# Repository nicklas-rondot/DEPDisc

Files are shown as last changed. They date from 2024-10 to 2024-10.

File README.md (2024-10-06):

# DEPDisc
The DEPDisc platform is the first implementation of dielectrophoresis where both the equipment and the consumables are truly inexpensive. It utilizes CD microfluidics to allow the integration of DEP with other microfluidic operations. 
All aspects of the DEPDisc platform are open-source, including the fabrication technique for the discs (with example designs) and the device.
While the paper presents the underlying theory and the results of the DEPDisc platform, this repository is intended to provide the necessary information to reproduce the platform.

This version is from the 06th of October 2024. A more current version might be available at https://github.com/nicklas-rn/DEPDisc.

## Table of Contents
- [Discs](#Discs)
- [Device](#Device)
- [How to Run](<#How to Run>)
- [Additional Figures](<#Additional Figures>)

## Discs
In the folder [Discs](/Discs), the design files for the discs can be found. The PCB files can be used in Eagle or Fusion360 Electronics. [Example Disc PCBs](/Discs/Example%20Disc%20PCBs) are provided as inspiration. The separate [coil PCB](/Discs/Coil%20PCB/) used as transmitter is included as well. For new designs, the [coil PCB library](/Discs/Coil%20PCB%20Library/) can be used.

## Device
The [Device CAD and PCB folder](/Device/) contains all the necessary files to reproduce the DEPDisc device. The device is composed of a PCB, off-the-shelf components, and a set of 3D printed parts. 

### PCB
To order the PCB at [JLCPCB](https://jlcpcb.com), the [Manufacturing folder](/Device/PCB/Manufacturing/) with a [ZIP file](/Device/PCB/Manufacturing/DEPDisc%20Base%20rev1%20v8_2024-09-17.zip) of the Gerber files is included. For assembly by JLCPCB, the [BOM file](/Device/PCB/Manufacturing/DEPDisc%20Base%20rev1%20v8_2024-09-17.zip) and [Pick and Place file](/Device/PCB/Manufacturing/DEPDisc%20Base%20rev1%20v8_2024-09-17.zip) are also provided. 
The ordering process is the follwing:
1. Go to [JLCPCB](https://jlcpcb.com)
2. Click on **Add gerber file** and upload the ZIP file
3. Select the desired options and **Enable PCB Assembly** (choose 2 as PCBA quantity instead of 5). Select **Bottom Side Assembly**.
4. After clicking **Next**, upload the **BOM file** and **CPL (Pick and Place) file**, then continue
5. When reviewing the parts, ensure that only C13 and JP3 show 'No part selected' and that the rest of the parts are correctly assigned. Then click **Next** and then **Do not Place** upon the prompt showing that the project has unselected parts.
6. Review the part placement and click **Next**, then click **Save to Cart**
7. Review the order and click **Secure Checkout**

The [design files](/Device/PCB/Design%20Files) of the PCB for Eagle or Fusion360 Electronics are included in case this project is used as inspiration or if modifications are desired.

### Housing
The [parts for printing](/Device/3D%20Printed%20Parts) are provided as STL files. In the slicer, we recommend enabling tree-supports. 
A [STEP file](/Device/DEPDisc%20Device%20rev1.step) of the assembly is included. 

### Assembly
To assemble the device, use the following procedure:
1. Place M3 nuts in all the provided slots in the 3D printed parts.
2. Solder the pin-headers to the PCB: 
3. Solder two jumper wires to the motor: 
4. Plug the ESP32 NodeMCU Dev board into the pin-headers: 
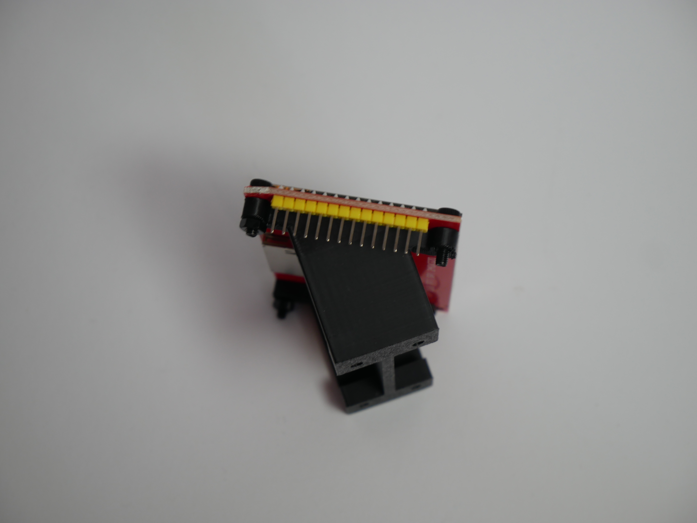
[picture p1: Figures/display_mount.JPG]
5. Screw the touch display to the display mount: 
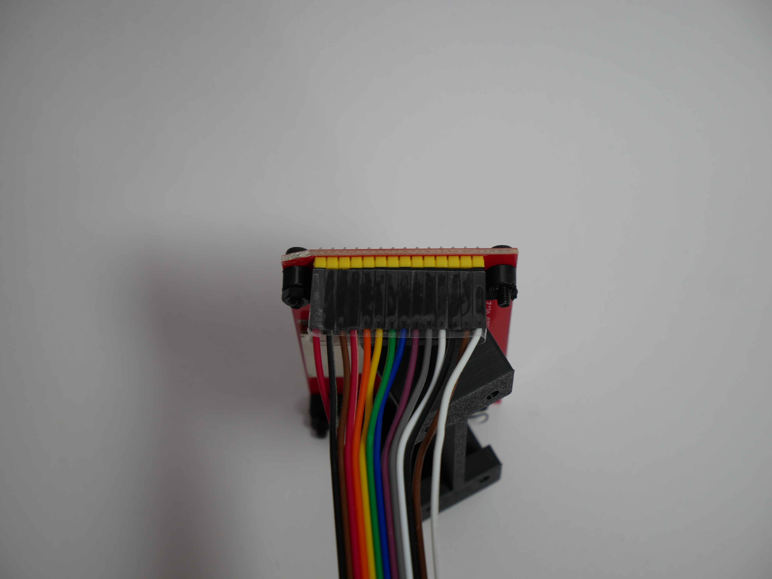
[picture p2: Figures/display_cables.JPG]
6. Plug in 14 female-to-female jumper wires to the display. We recommend placing tape around the ends to keep the wires together when they are removed: 
7. Plug the other side of the jumper wires into the PCB: 
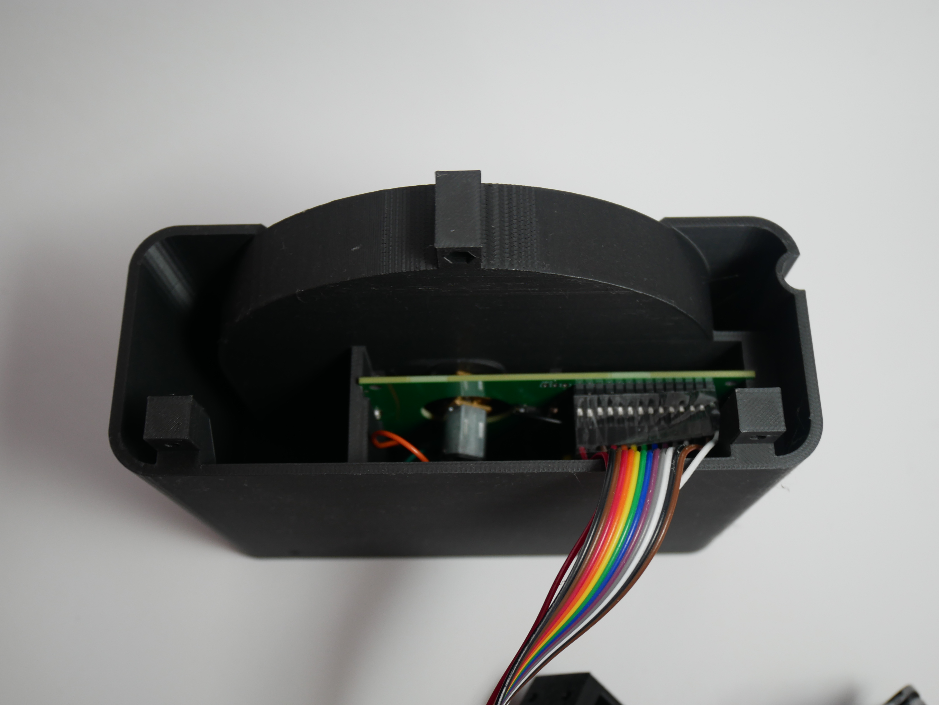
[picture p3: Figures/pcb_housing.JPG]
8. Slide the PCB into the left side of the inner shell of the housing and move the motor through the hole: 
9. Screw the motor in place with two M1.2 screws: 
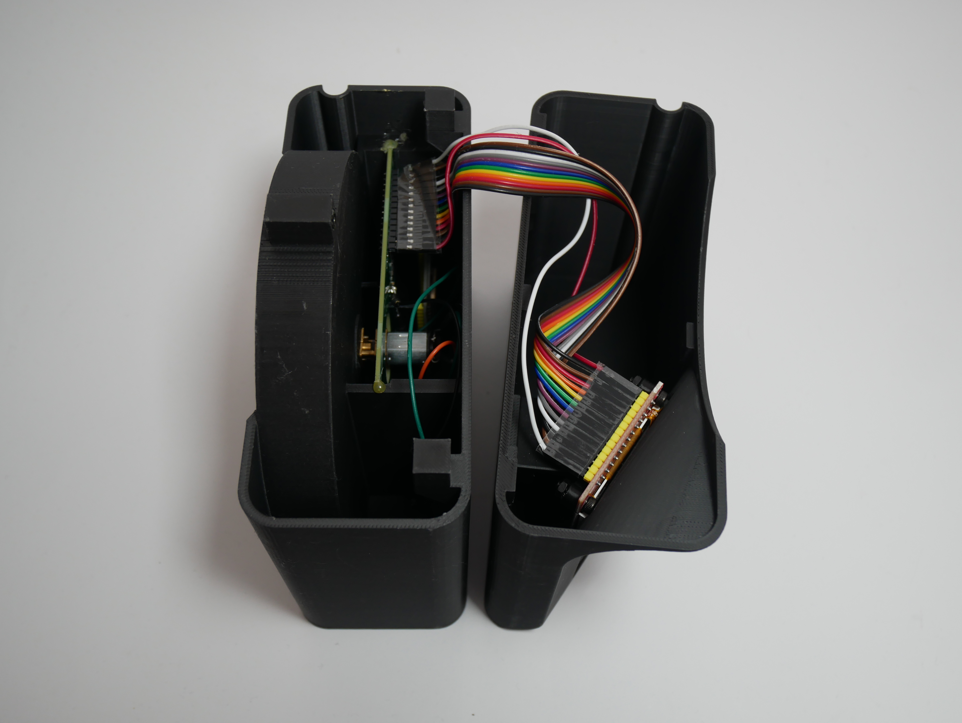
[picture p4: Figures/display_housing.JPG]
10. Slide the display in to the right side of the inner shell of the housing: 
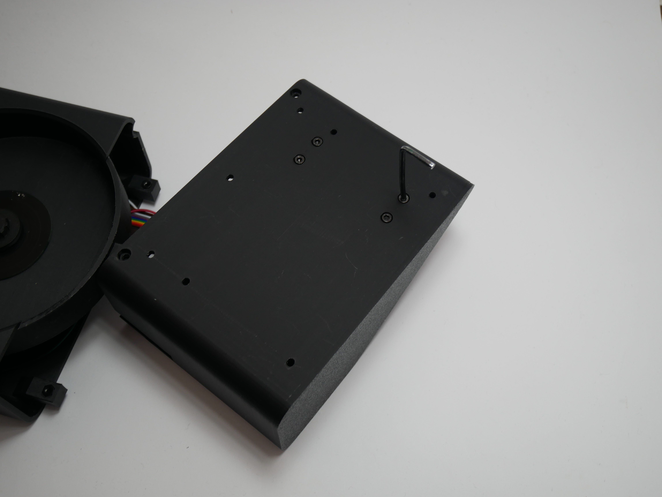
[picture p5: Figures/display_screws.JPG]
11. Screw the display in place from the bottom with four M3 screws: 
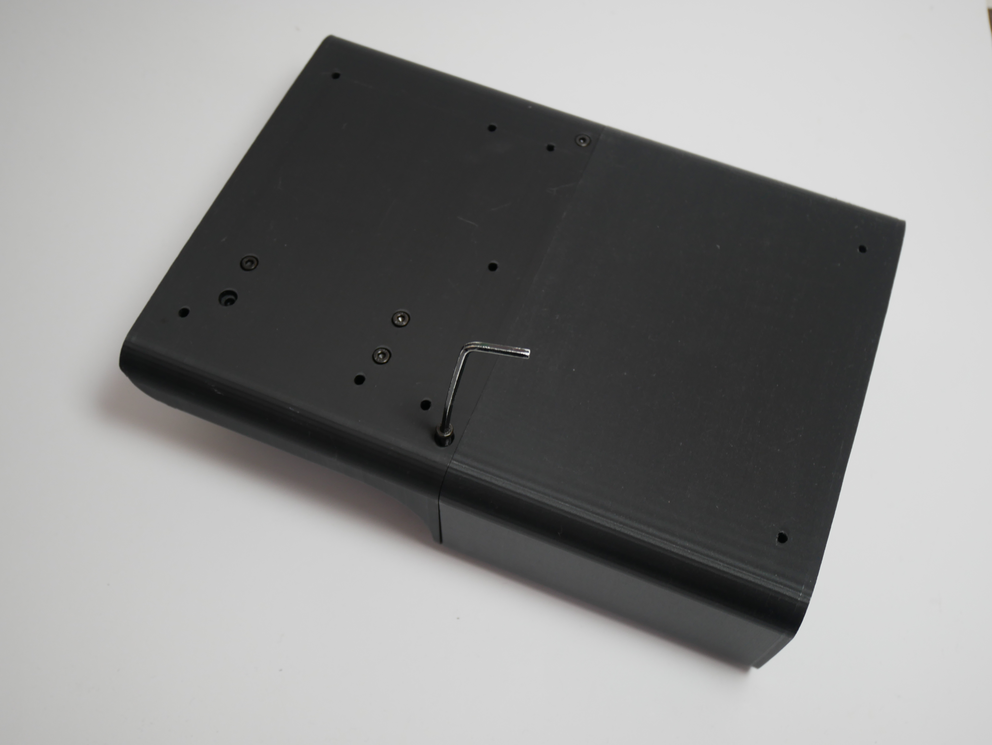
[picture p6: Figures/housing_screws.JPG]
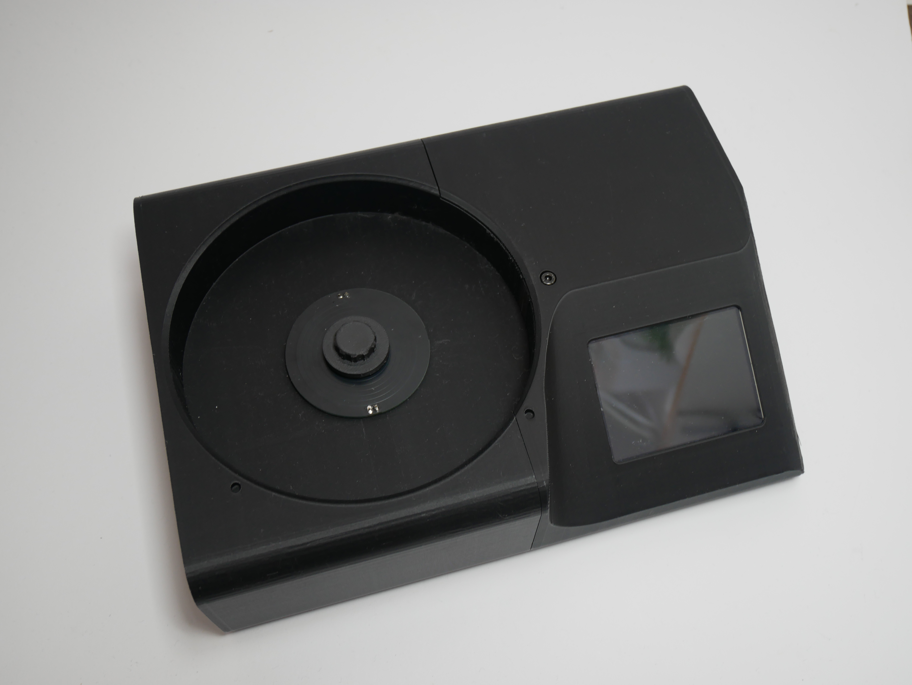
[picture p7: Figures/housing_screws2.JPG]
12. Connect the two inner shell sides with three M3 screws:  
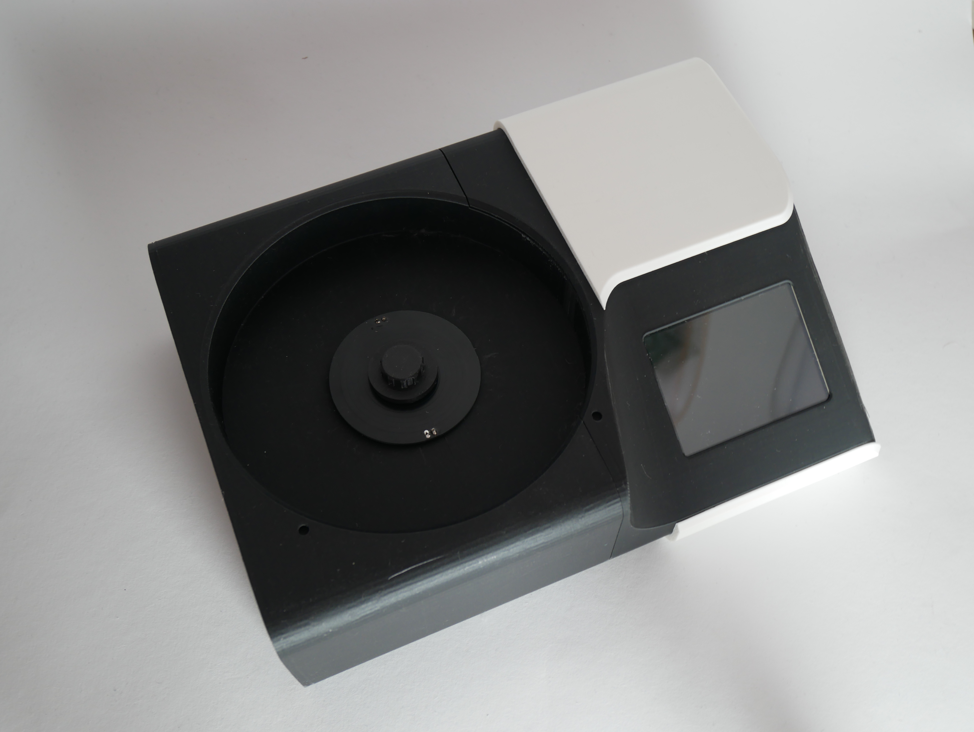
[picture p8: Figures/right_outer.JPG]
13. Place the right side of the outer shell on top of the inner shell by carefully bending it slightly: 
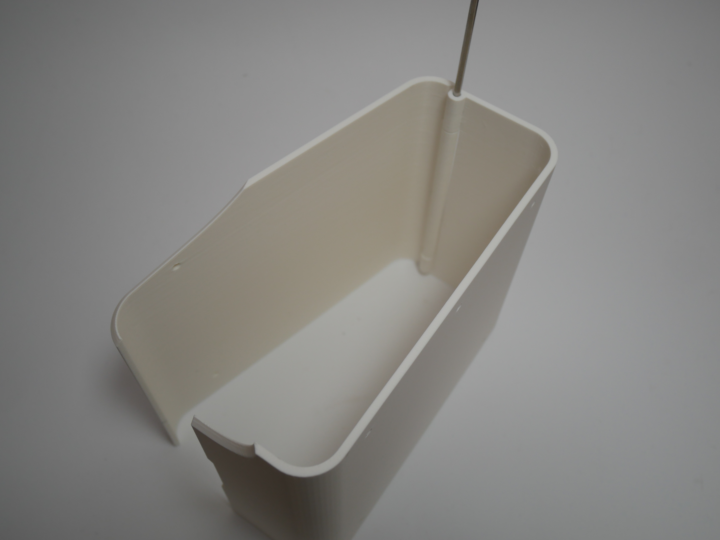
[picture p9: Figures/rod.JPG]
14. Push the aluminium rod through the left side of the outer shell and the hatch: 
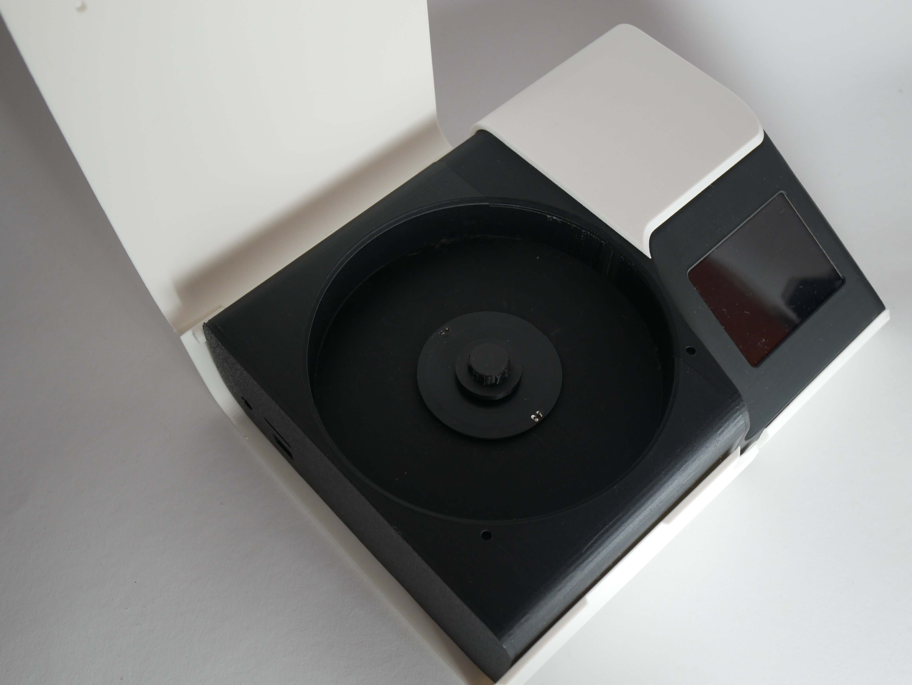
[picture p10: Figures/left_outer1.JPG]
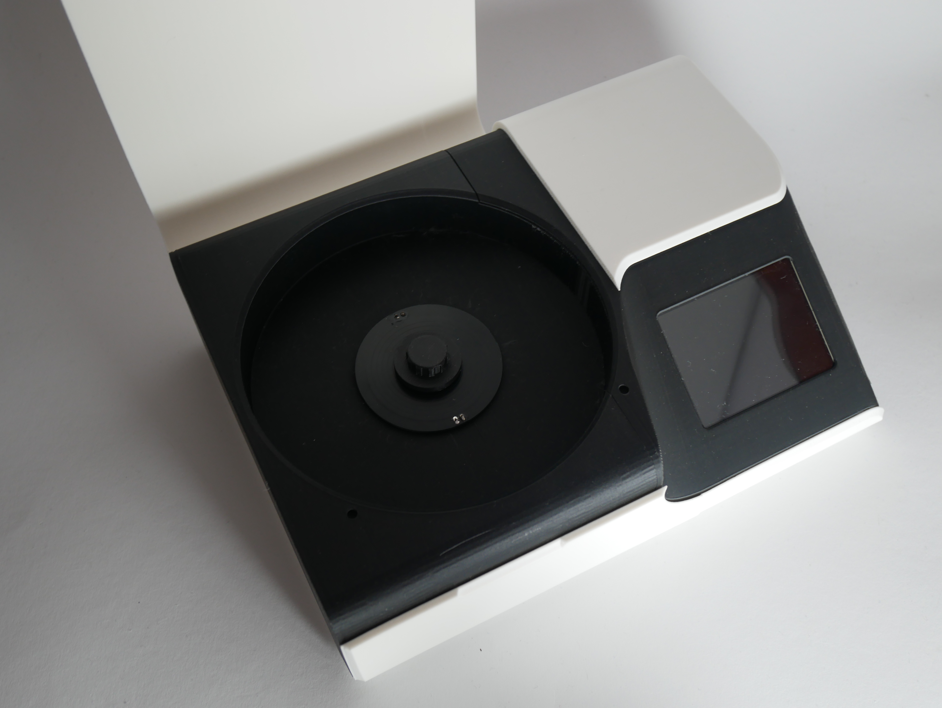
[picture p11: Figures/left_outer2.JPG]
15. Push the left side of the outer shell on top of the inner shell by moving it in from the left and carefully bending it slightly:  
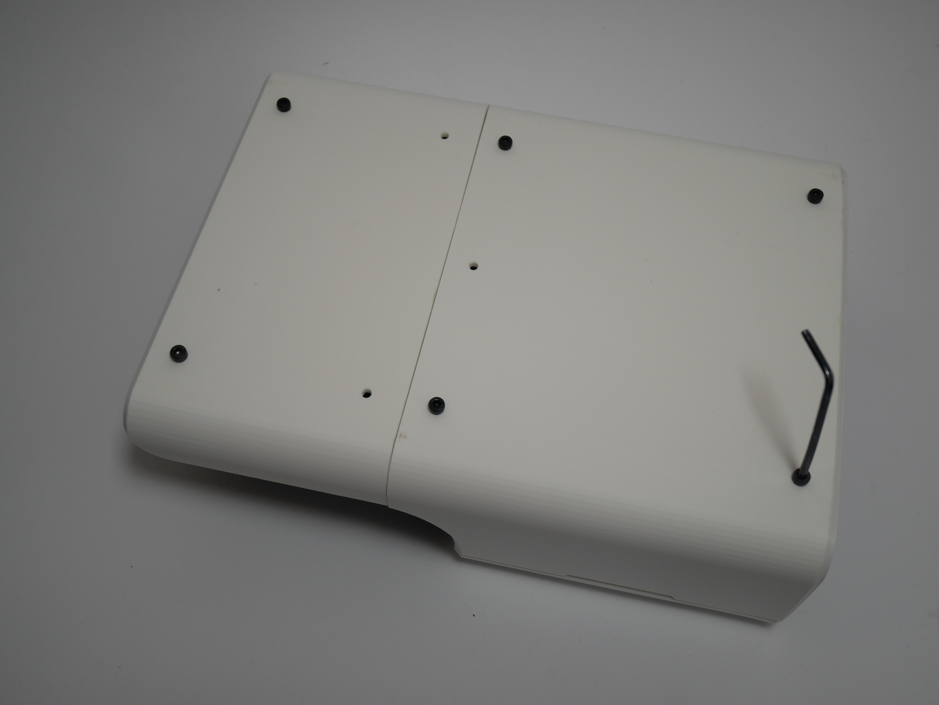
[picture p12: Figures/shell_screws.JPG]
16. Screw six M3 screws into the outer shell: 

### Programming
To program the device, use the [Arduino file](/Device/Software/DEPDisc_base.ino) provided in the [Software folder](/Device/Software). Use to following procedure:
1. Download the Arduino IDE
2. Install the ESP32 boards under the boards manager (Second tab from the top, type 'esp32' in the search bar, and click install)
3. Click on Tools -> Board -> esp32 -> ESP32 Dev Module
4. Select the correct port under Tools -> Port
5. Click on the upload button (right arrow) to upload the code to the ESP32

## How to Run
### Experimental mode
Connect the device with a USB cable to a laptop. Use the Serial Monitor of the Arduino IDE and select a Baud Rate of 115200. 
To set a specific frequency, type: `freq [frequency in Hz]`
To set a specific speed, type: spin `[PWM value between -255 and 255]`

### Run from SD card
Write a text file with the name **run.txt** to the SD card with the same commands as above. Between the commands use a newline. Use the command `delay [delay in seconds]` to set delays. Insert the SD card into the device and select 'Run from SD card'. The device will read the file and execute the commands.

## Additional Figures
- [A video showing the attraction of yeast cells to the edges of two electrodes](/Figures/dep_edge.mov).

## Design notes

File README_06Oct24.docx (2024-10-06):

# DEPDisc

The DEPDisc platform is the first implementation of dielectrophoresis where both the equipment and the consumables are truly inexpensive. It utilizes CD microfluidics to allow the integration of DEP with other microfluidic operations. All aspects of the DEPDisc platform are open-source, including the fabrication technique for the discs (with example designs) and the device. While the paper presents the underlying theory and the results of the DEPDisc platform, this repository is intended to provide the necessary information to reproduce the platform.

This version is from the 06th of October 2024. A more current version might be available at https://github.com/nicklas-rn/DEPDisc.
This Word file is a converted version of the README.md file found in the repository. Therefore, hyperlinks to folders might not work here.

## Table of Contents

- Discs
- Device
- How to Run
- Additional Figures

## Discs

In the folder Discs, the design files for the discs can be found. The PCB files can be used in Eagle or Fusion360 Electronics. Example Disc PCBs are provided as inspiration. The separate coil PCB used as transmitter is included as well. For new designs, the coil PCB library can be used.

## Device

The Device CAD and PCB folder contains all the necessary files to reproduce the DEPDisc device. The device is composed of a PCB, off-the-shelf components, and a set of 3D printed parts.

### PCB

To order the PCB at JLCPCB (https://jlcpcb.com), the Manufacturing folder with a ZIP file of the Gerber files is included. For assembly by JLCPCB, the BOM file and Pick and Place file are also provided. The ordering process is the follwing:

1. Go to JLCPCB (https://jlcpcb.com)
2. Click on Add gerber file and upload the ZIP file
3. Select the desired options and Enable PCB Assembly (choose 2 as PCBA quantity instead of 5). Select Bottom Side Assembly.
4. After clicking Next, upload the BOM file and CPL (Pick and Place) file, then continue
5. When reviewing the parts, ensure that only C13 and JP3 show ‘No part selected’ and that the rest of the parts are correctly assigned. Then click Next and then Do not Place upon the prompt showing that the project has unselected parts.
6. Review the part placement and click Next, then click Save to Cart
7. Review the order and click Secure Checkout

The design files of the PCB for Eagle or Fusion360 Electronics are included in case this project is used as inspiration or if modifications are desired.

### Housing

The parts for printing are provided as STL files. In the slicer, we recommend enabling tree-supports. A STEP file of the assembly is included.

### Assembly

To assemble the device, use the following procedure:

1. Place M3 nuts in all the provided slots in the 3D printed parts.
2. Solder the pin-headers to the PCB:

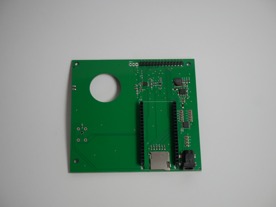
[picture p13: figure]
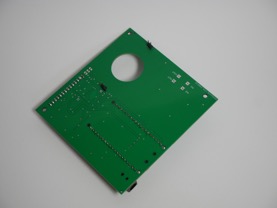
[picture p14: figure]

3. Solder two jumper wires to the motor:

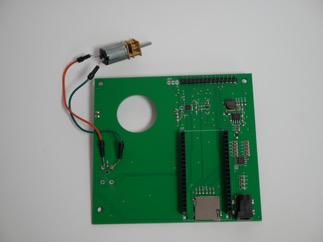
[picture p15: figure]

4. Plug the ESP32 NodeMCU Dev board into the pin-headers:

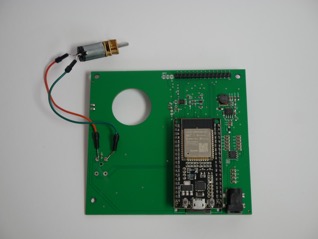
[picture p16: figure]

5. Screw the touch display to the display mount:

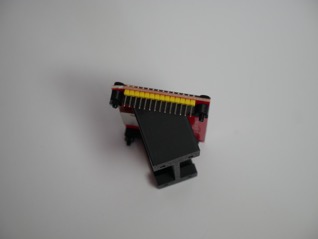
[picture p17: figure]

6. Plug in 14 female-to-female jumper wires to the display. We recommend placing tape around the ends to keep the wires together when they are removed:

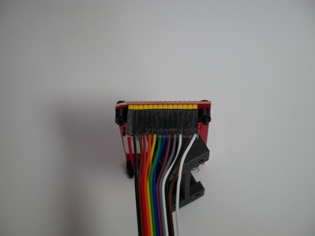
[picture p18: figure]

7. Plug the other side of the jumper wires into the PCB.

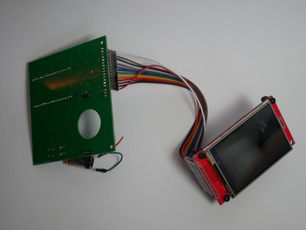
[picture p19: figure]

8. Slide the PCB into the left side of the inner shell of the housing and move the motor through the hole:

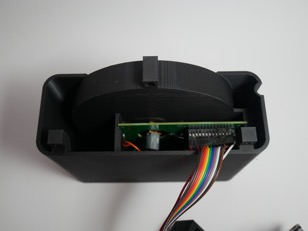
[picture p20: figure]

9. Screw the motor in place with two M1.2 screws:

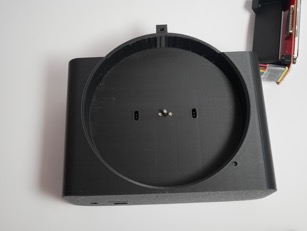
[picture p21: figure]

10. Slide the display in to the right side of the inner shell of the housing:

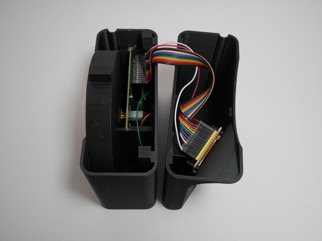
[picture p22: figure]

11. Screw the display in place from the bottom with four M3 screws:

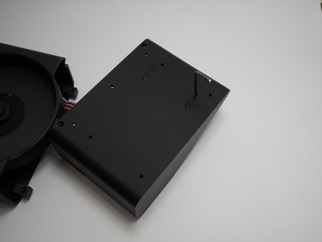
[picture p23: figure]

12. Connect the two inner shell sides with three M3 screws:

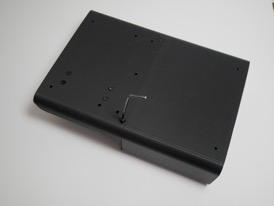
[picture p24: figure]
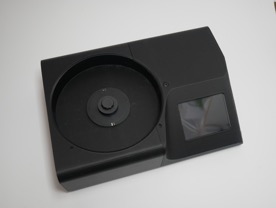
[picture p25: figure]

13. Place the right side of the outer shell on top of the inner shell by carefully bending it slightly:

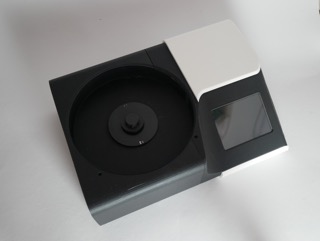
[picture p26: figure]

14. Push the aluminium rod through the left side of the outer shell and the hatch:

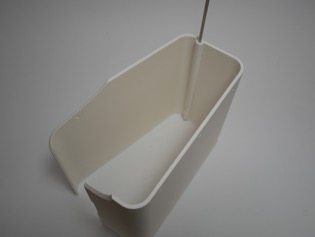
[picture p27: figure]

15. Push the left side of the outer shell on top of the inner shell by moving it in from the left and carefully bending it slightly:

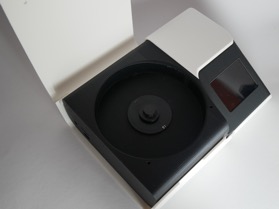
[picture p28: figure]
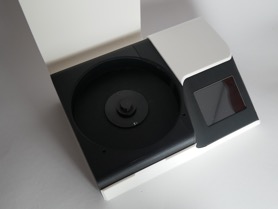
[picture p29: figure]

16. Screw six M3 screws into the outer shell:

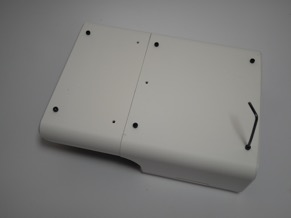
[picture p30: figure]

### Programming

To program the device, use the Arduino file provided in the Software folder. Use to following procedure:

1. Download the Arduino IDE
2. Install the ESP32 boards under the boards manager (Second tab from the top, type ‘esp32’ in the search bar, and click install)
3. Click on Tools -> Board -> esp32 -> ESP32 Dev Module
4. Select the correct port under Tools -> Port
5. Click on the upload button (right arrow) to upload the code to the ESP32

## How to Run

### Experimental mode

Connect the device with a USB cable to a laptop. Use the Serial Monitor of the Arduino IDE and select a Baud Rate of 115200. To set a specific frequency, type: freq [frequency in Hz]. To set a specific speed, type: spin [PWM value between -255 and 255]

### Run from SD card

Write a text file with the name run.txt to the SD card with the same commands as above. Between the commands use a newline. Use the command delay [delay in seconds] to set delays. Insert the SD card into the device and select ‘Run from SD card’. The device will read the file and execute the commands.

## Additional Figures

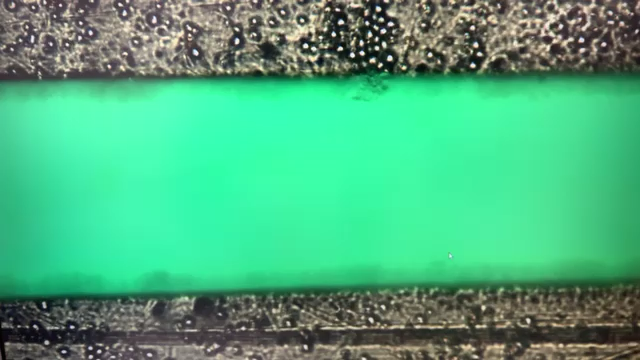
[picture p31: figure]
movie::/Users/nicklasrondot/Documents/Lab on a Disc/DEPDisc/Figures/dep_edge.mov

(/Figures/dep_edge.mov)

A video showing the attraction of yeast cells to the edges of two electrodes. A 3.5 MHz signal was applied 6 seconds after the start of the video.

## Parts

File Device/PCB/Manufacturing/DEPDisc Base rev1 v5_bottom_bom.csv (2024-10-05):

Comment | Designator | Footprint | LCSC Part #
1N5819WS | D9 D10 | SOD323-W
1k | R6 R10 | R0603
1nF | C2 | C0603K
2k | R13 R20 R28 | R0603
10k | R24A | R0603
10nF | C1 C17 | C0603K
10uF | C19 | C0603K
22uF | C5 C6 C7 C8 C11 C12 C14 C20 C21 C22 C23 C24 C25 C26 | C0805K
29.4k | R22 | R0603
47k | R1 R2 R3 R16 R17 R18 | R0603
47pF | C3 | C0603K
47uF | C10 C16 | C0603K
68.1k | R21 | R0603
100nF | C4 C9 C15 C18 | C0603K
332k | R19 | R0603
510 | R4 R5 R24B | R0603
750 | R25 R30 | R0603
1255AY-6R8M=P3 | L2 | IND_1255AY-6R8M=P3
DC-005-2.5A-2.0-SMT | CN1 | DCJACK_2MM_SMT
DNP | C13 | C0805K
DRV8220DRLRSOT5X3-6_DRL_TEX-L | U5 | SOT5X3-6_DRL_TEX-L
ICL7662EBA-T | U4 | 21-0041B_8
JUMPER-SMT_2_NC_PASTE_SILK | JP3 | SMT-JUMPER_2_NC_PASTE_SILK
MICROSD-PUSH-OUT | U$2 | MICROSD-PUSH-OUT
OPA2810IDGKR | U$1 | SOP65P490X110-8N
SN74LVC2G04DCKR | U3 | SOT65P210X110-6N
TPS54331DR | U1 | SOIC127P599X175-8N

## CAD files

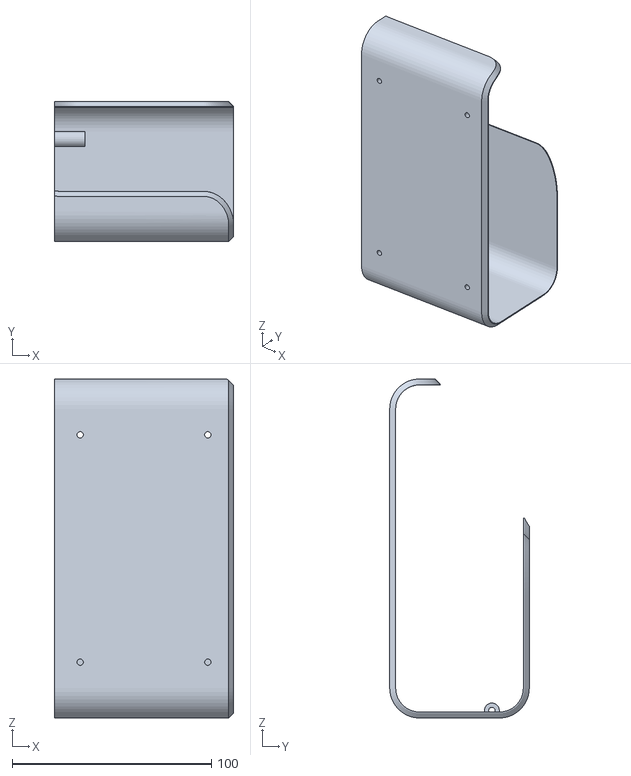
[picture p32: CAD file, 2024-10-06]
Device/3D Printed Parts/Outer Shell right (white).stl
90.0 x 70.0 x 170.0

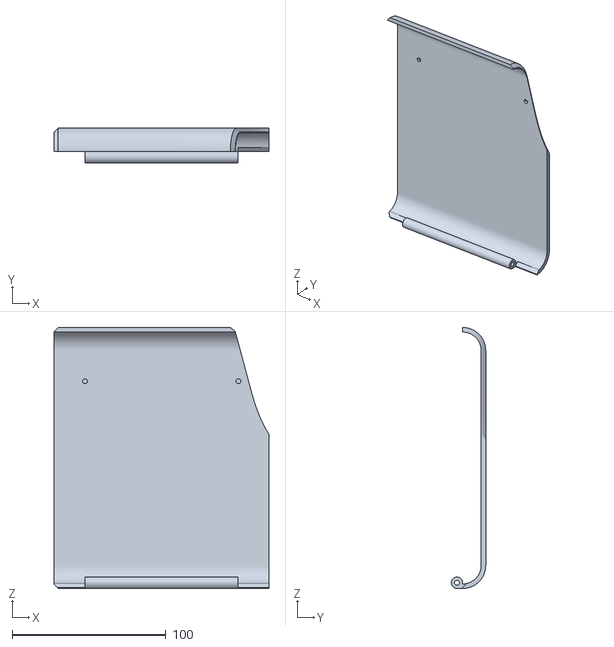
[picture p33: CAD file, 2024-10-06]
Device/3D Printed Parts/Hatch (white).stl
139.8 x 22.5 x 170.0

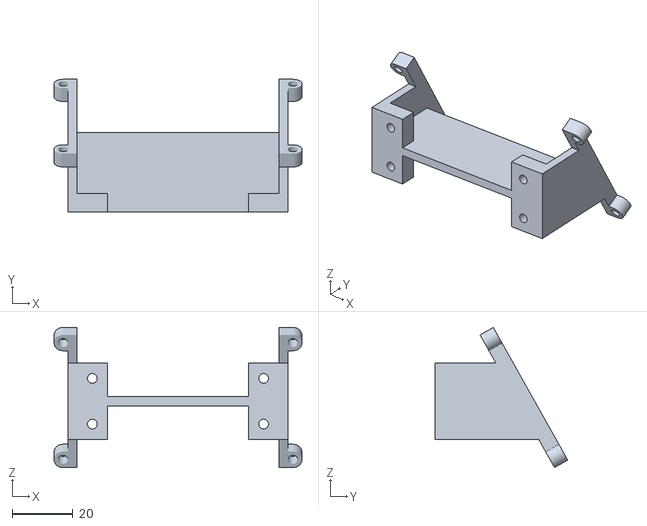
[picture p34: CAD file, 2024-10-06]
Device/3D Printed Parts/Display Holder (black).stl
81.5 x 43.5 x 46.1

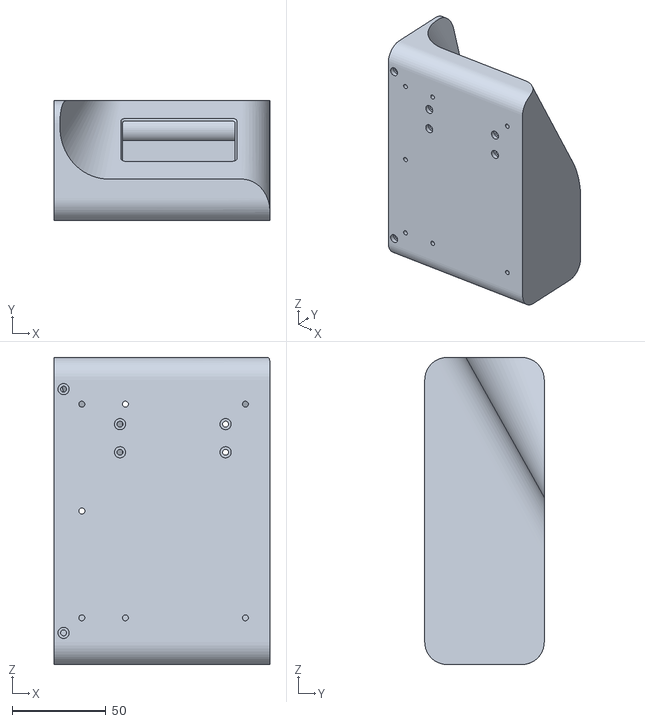
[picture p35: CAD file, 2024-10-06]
Device/3D Printed Parts/Inner Shell right (black).stl
115.0 x 63.8 x 163.8

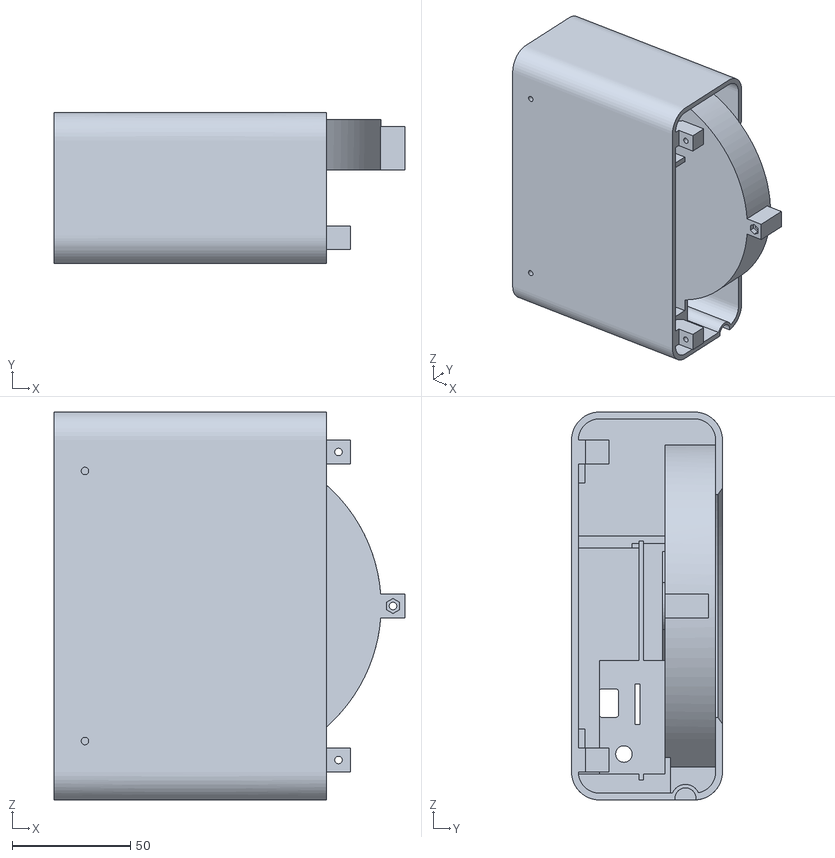
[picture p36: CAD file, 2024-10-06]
Device/3D Printed Parts/Inner Shell left (black).stl
148.0 x 63.8 x 163.8

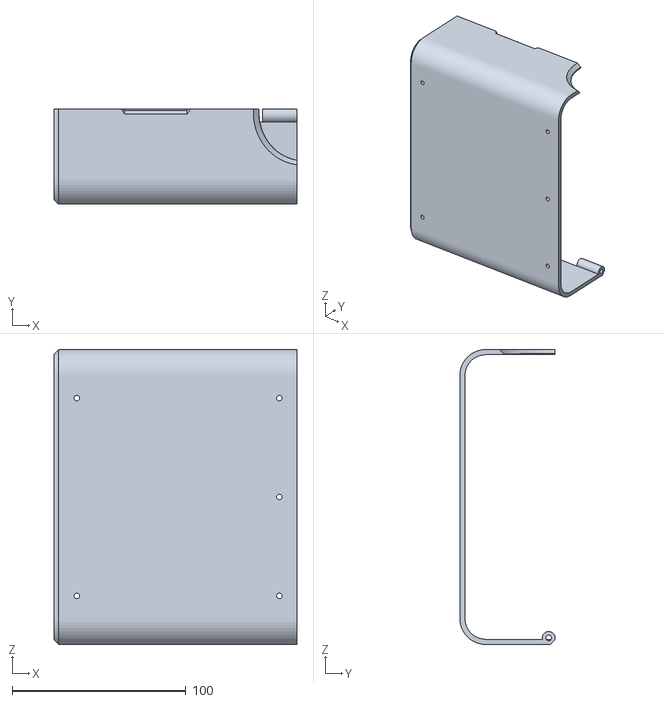
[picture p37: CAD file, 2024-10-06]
Device/3D Printed Parts/Outer Shell left (white).stl
139.8 x 55.0 x 170.0

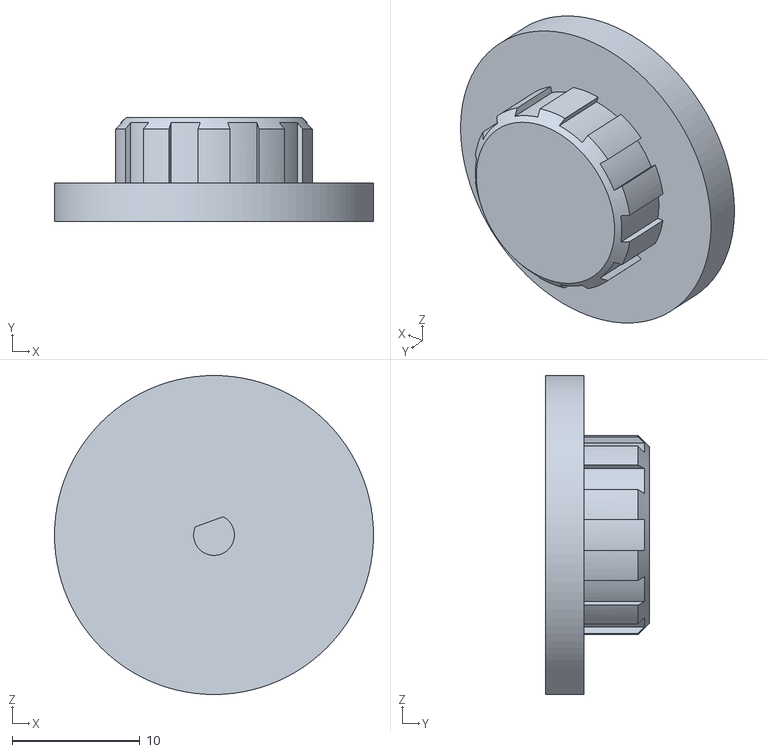
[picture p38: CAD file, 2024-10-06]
Device/3D Printed Parts/Disc Mount (black).stl
25.0 x 8.15 x 25.0

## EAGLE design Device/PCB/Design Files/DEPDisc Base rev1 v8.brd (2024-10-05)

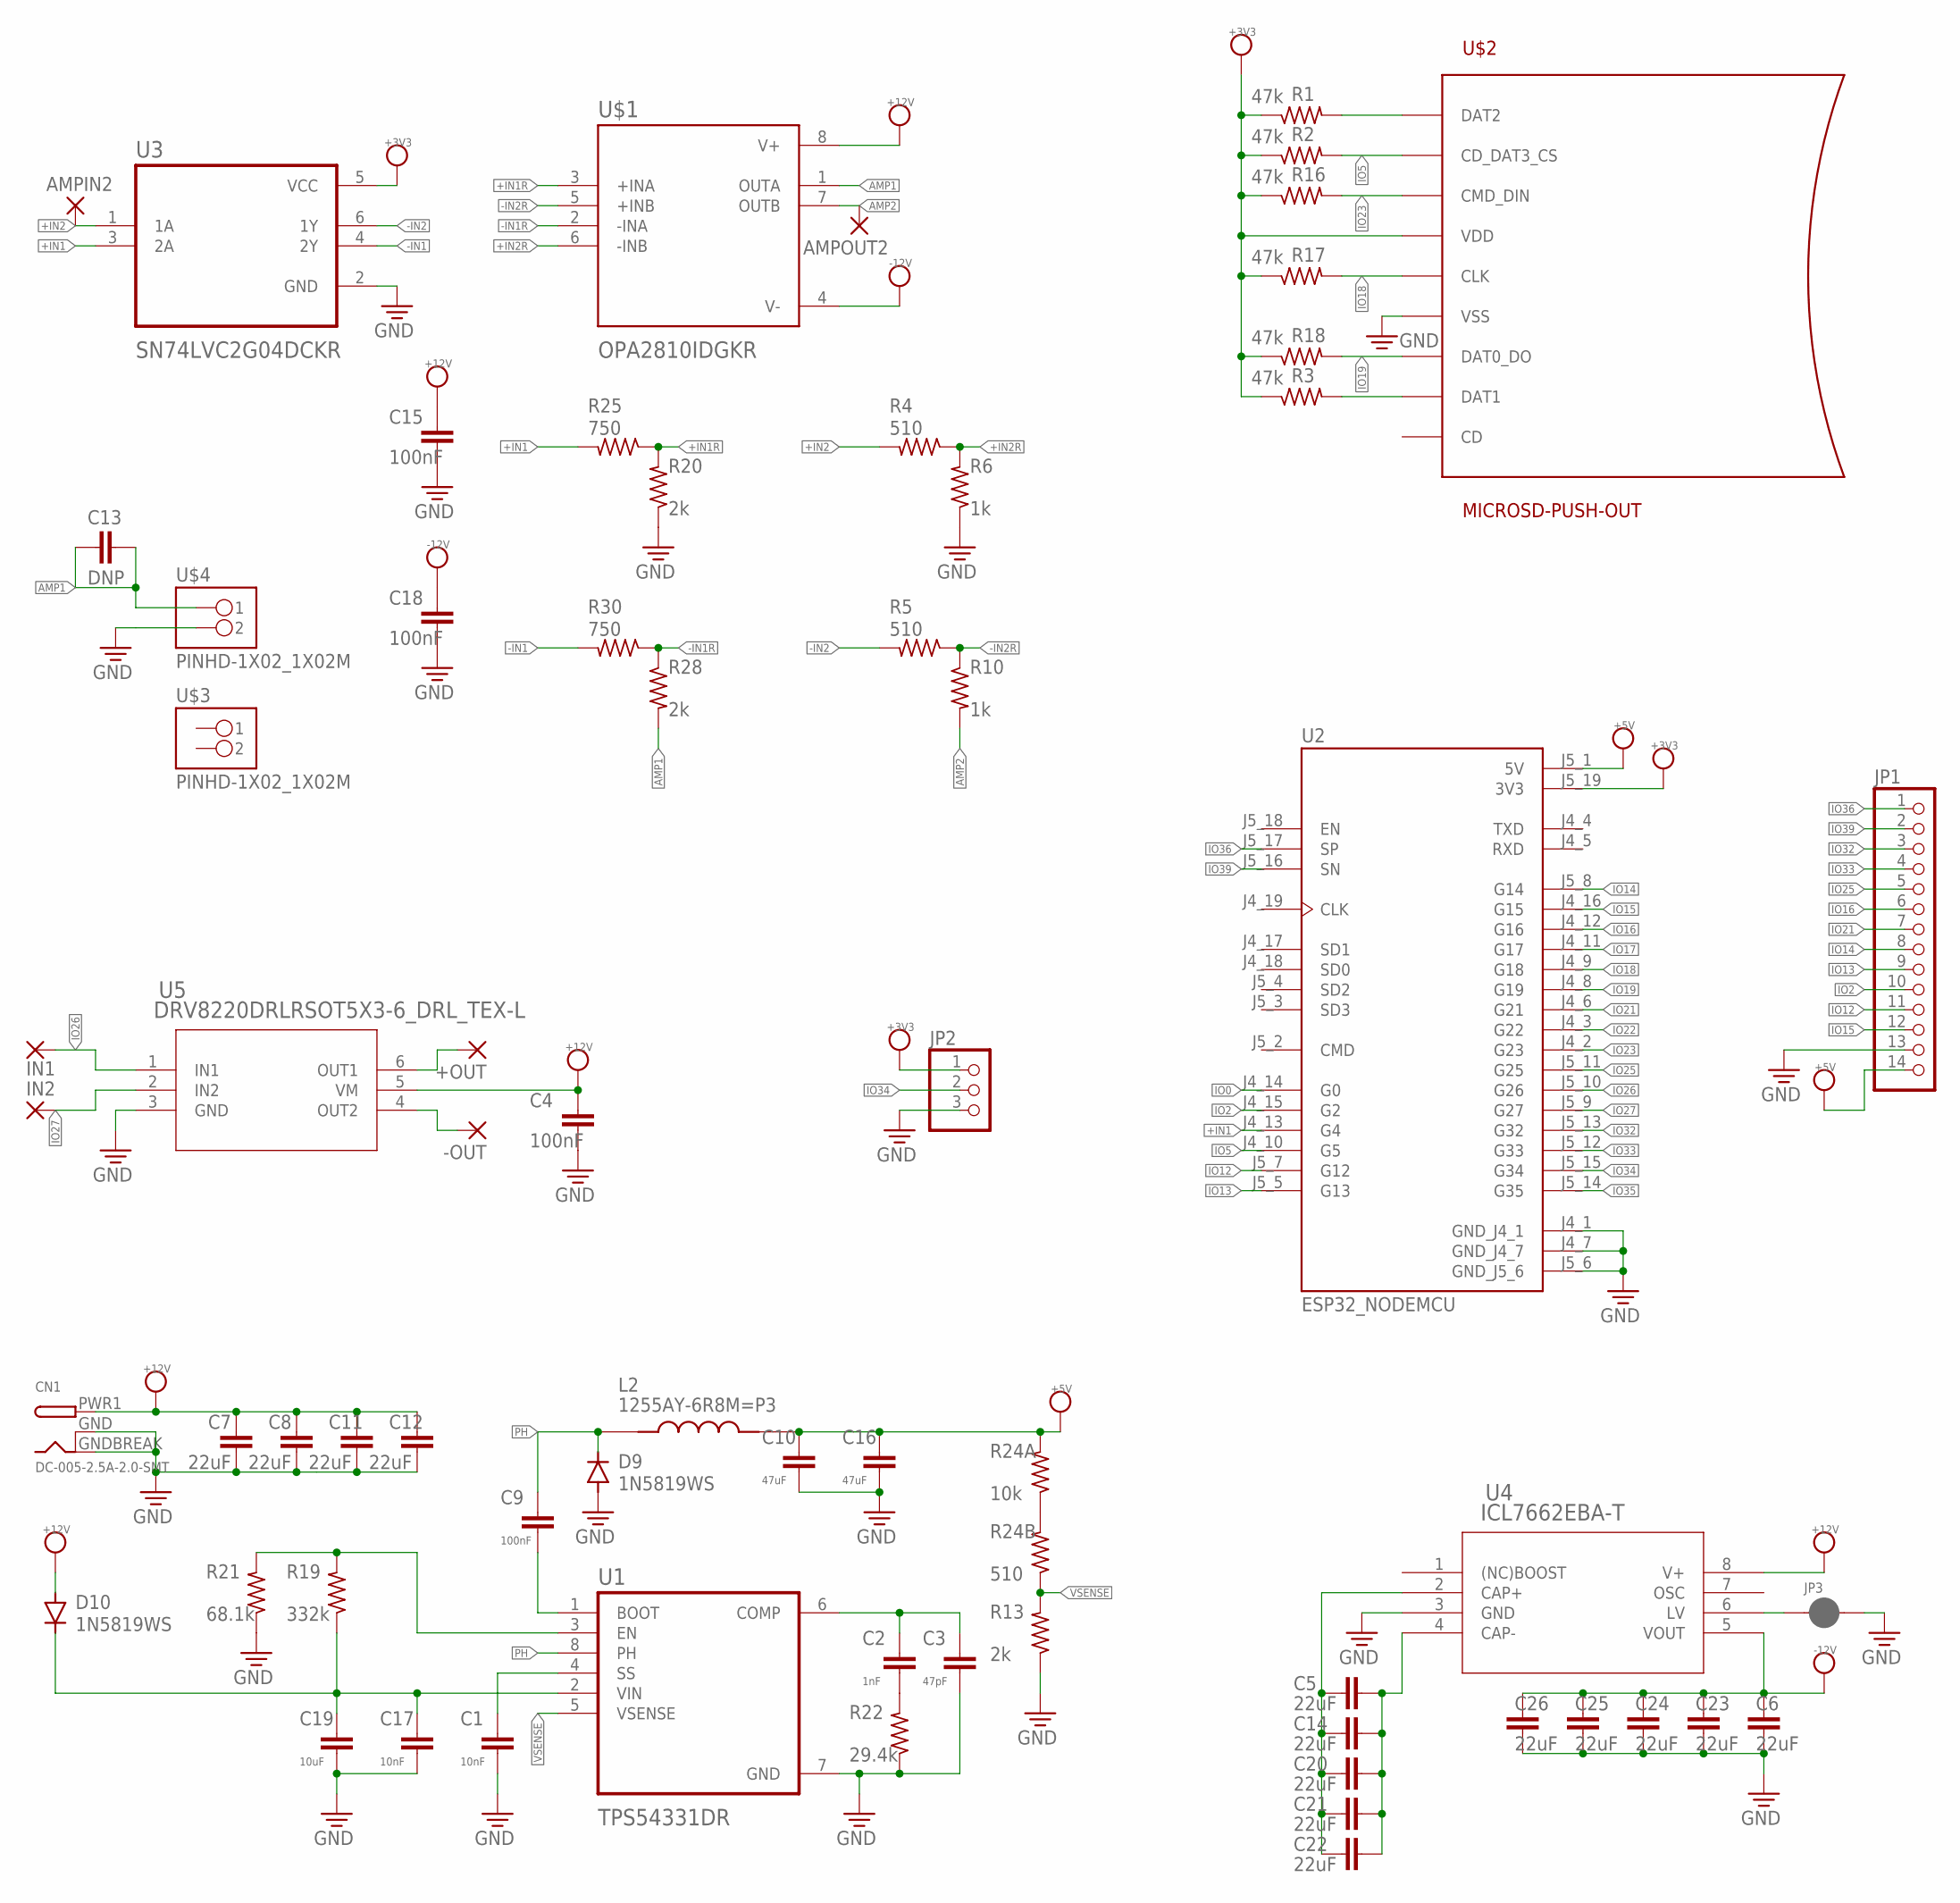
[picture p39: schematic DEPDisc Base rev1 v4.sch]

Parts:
+OUT: 2,54/1,1
-OUT: 2,54/1,1
AMPIN2: 1,6/0,8
AMPOUT2: 1,6/0,8
C1, C17: 10nF; C0603K
C2: 1nF; C0603K
C3: 47pF; C0603K
C4, C9, C15, C18: 100nF; C0603K
C5, C6, C7, C8, C11, C12, C14, C20, C21, C22, C23, C24, C25, C26: 22uF; C0805K
C10, C16: 47uF; C0603K
C13: DNP; C0805K
C19: 10uF; C0603K
CN1: DC-005-2.5A-2.0-SMT; DCJACK_2MM_SMT
D9, D10: 1N5819WS; SOD323-W
IN1, IN2: 2,54/1,1
JP1: PINHD-1X14; 1X14
JP2: PINHD-1X3; 1X03
JP3: JUMPER-SMT_2_NC_PASTE_SILK; SMT-JUMPER_2_NC_PASTE_SILK
L2: 1255AY-6R8M=P3; IND_1255AY-6R8M=P3
R1, R2, R3, R16, R17, R18: 47k; R0603
R4, R5, R24B: 510; R0603
R6, R10: 1k; R0603
R13, R20, R28: 2k; R0603
R19: 332k; R0603
R21: 68.1k; R0603
R22: 29.4k; R0603
R24A: 10k; R0603
R25, R30: 750; R0603
U1: TPS54331DR; SOIC127P599X175-8N
U2: ESP32_NODEMCU; MODULE_ESP32_NODEMCU
U3: SN74LVC2G04DCKR; SOT65P210X110-6N
U4: ICL7662EBA-T; 21-0041B_8
U5: DRV8220DRLRSOT5X3-6_DRL_TEX-L; SOT5X3-6_DRL_TEX-L
U$1: OPA2810IDGKR; SOP65P490X110-8N
U$2: MICROSD-PUSH-OUT
U$3, U$4: PINHD-1X02_1X02M; 1X02

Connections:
+3V3: JP2.1, R1.1, R2.1, R3.1, R16.1, R17.1, R18.1, U2.J5_19 (3V3), U3.5 (VCC), U$2.4 (VDD)
+5V: C10.1, C16.1, JP1.14, L2.2, R24A.2, U2.J5_1 (5V)
+12V: C4.1, C7.2, C8.2, C11.2, C12.2, C15.1, CN1.PWR1 (PWR), D10.A, U4.8 (V+), U5.5 (VM), U$1.8 (V+)
+IN1: R25.2, U2.J4_13 (G4), U3.3 (2A)
+IN1R: R20.2, R25.1, U$1.3 (+INA)
+IN2: AMPIN2.1, R4.2, U3.1 (1A)
+IN2R: R4.1, R6.2, U$1.6 (-INB)
-12V: C6.2, C18.1, C23.2, C24.2, C25.2, C26.2, U4.5 (VOUT), U$1.4 (V-)
-IN1: R30.2, U3.4 (2Y)
-IN1R: R28.1, R30.1, U$1.2 (-INA)
-IN2: R5.2, U3.6 (1Y)
-IN2R: R5.1, R10.1, U$1.5 (+INB)
AMP1: C13.1, C13.2, R28.2, U$1.1 (OUTA), U$4.1
AMP2: AMPOUT2.1, R10.2, U$1.7 (OUTB)
DAT2: R1.2, U$2.1 (DAT2)
GND: C1.2, C3.2, C4.2, C6.1, C7.1, C8.1, C10.2, C11.1, C12.1, C15.2, C16.2, C17.2, C18.2, C19.2, C23.1, C24.1, C25.1, C26.1, CN1.GND (GNDBREAK), CN1.GNDBREAK (GND), D9.A, JP1.13, JP2.3, JP3.2, R6.1, R13.1, R20.1, R21.1, R22.1, U1.7 (GND), U2.J4_1 (GND_J4_1), U2.J4_7 (GND_J4_7), U2.J5_6 (GND_J5_6), U3.2 (GND), U4.3 (GND), U5.3 (GND), U$2.6 (VSS), U$2.G1 (VSS), U$2.G2 (VSS), U$2.G3 (VSS), U$2.G4 (VSS), U$4.2
IO0: U2.J4_14 (G0)
IO2: JP1.10, U2.J4_15 (G2)
IO5: R2.2, U2.J4_10 (G5), U$2.2 (CD_DAT3_CS)
IO12: JP1.11, U2.J5_7 (G12)
IO13: JP1.9, U2.J5_5 (G13)
IO14: JP1.8, U2.J5_8 (G14)
IO15: JP1.12, U2.J4_16 (G15)
IO16: JP1.6, U2.J4_12 (G16)
IO17: U2.J4_11 (G17)
IO18: R17.2, U2.J4_9 (G18), U$2.5 (CLK)
IO19: R18.2, U2.J4_8 (G19), U$2.7 (DAT0_DO)
IO21: JP1.7, U2.J4_6 (G21)
IO22: U2.J4_3 (G22)
IO23: R16.2, U2.J4_2 (G23), U$2.3 (CMD_DIN)
IO25: JP1.5, U2.J5_11 (G25)
IO26: IN1.1, U2.J5_10 (G26), U5.1 (IN1)
IO27: IN2.1, U2.J5_9 (G27), U5.2 (IN2)
IO32: JP1.3, U2.J5_13 (G32)
IO33: JP1.4, U2.J5_12 (G33)
IO34: JP2.2, U2.J5_15 (G34)
IO35: U2.J5_14 (G35)
IO36: JP1.1, U2.J5_17 (SP)
IO39: JP1.2, U2.J5_16 (SN)
unnamed: C5.2, C14.2, C20.2, C21.2, C22.2, U4.2 (CAP+)
unnamed: C5.1, C14.1, C20.1, C21.1, C22.1, U4.4 (CAP-)
unnamed: +OUT.1, U5.6 (OUT1)
unnamed: -OUT.1, U5.4 (OUT2)
unnamed: JP3.1, U4.6 (LV)
unnamed: R19.2, R21.2, U1.3 (EN)
unnamed: C1.1, U1.4 (SS)
unnamed: R3.2, U$2.8 (DAT1)
unnamed: C2.1, C3.1, U1.6 (COMP)
unnamed: C2.2, R22.2
unnamed: R24A.1, R24B.2
unnamed: C9.2, U1.1 (BOOT)
unnamed: C17.1, C19.1, D10.C, R19.1, U1.2 (VIN)
PH: C9.1, D9.C, L2.1, U1.8 (PH)
VSENSE: R13.2, R24B.1, U1.5 (VSENSE)

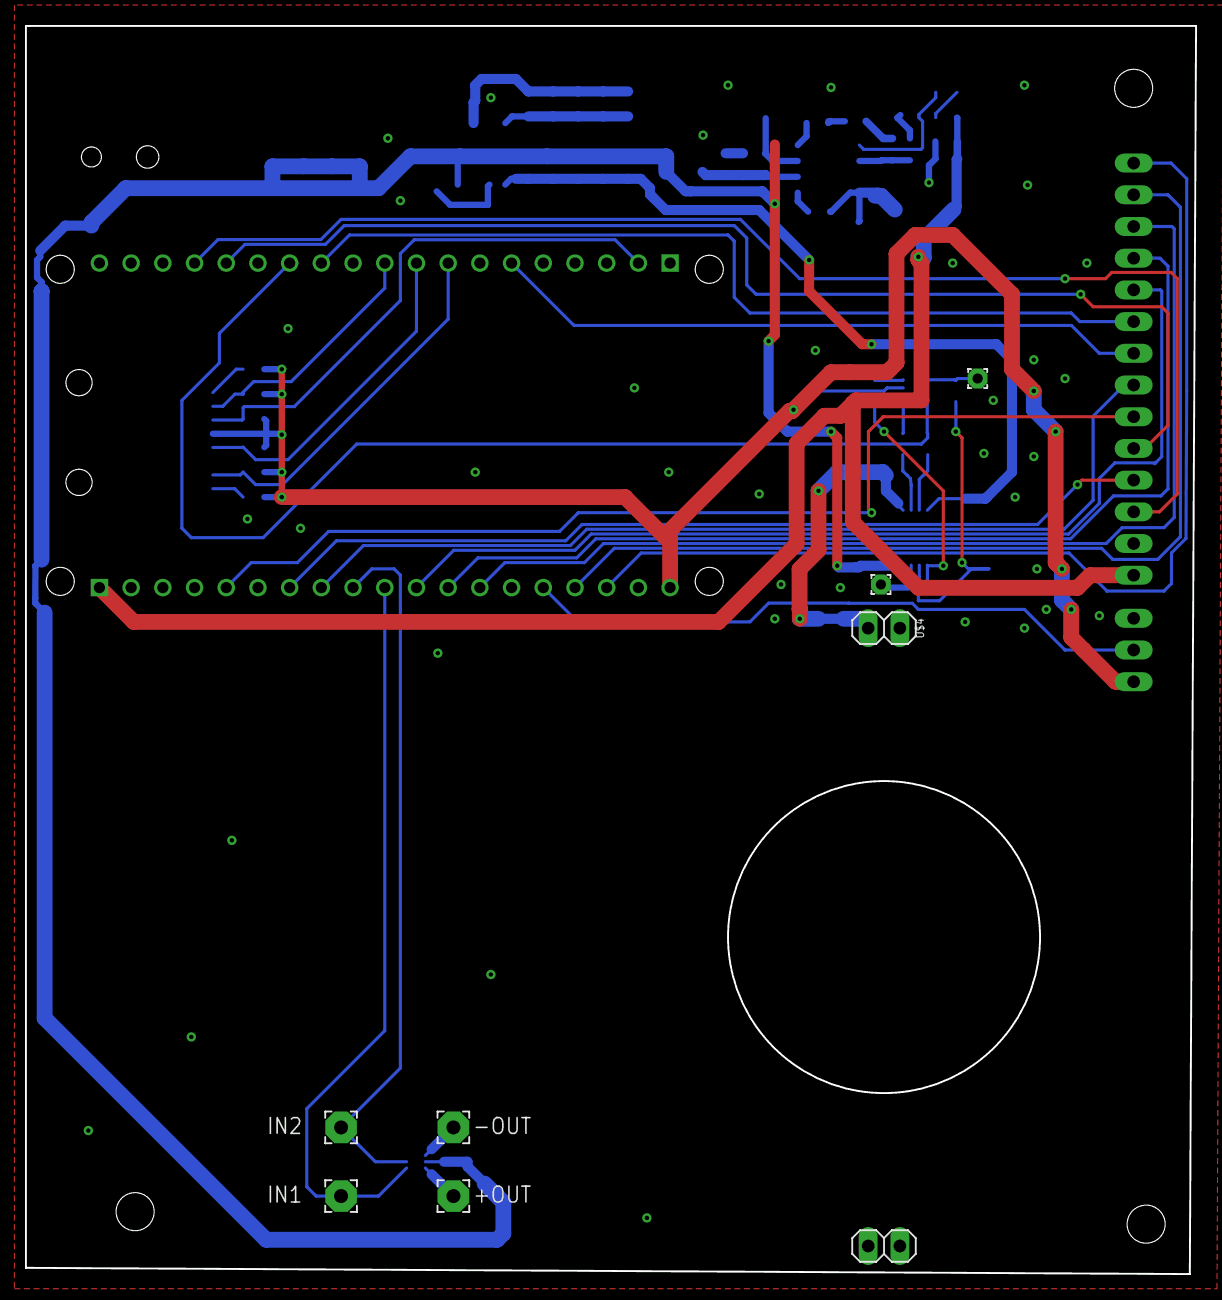
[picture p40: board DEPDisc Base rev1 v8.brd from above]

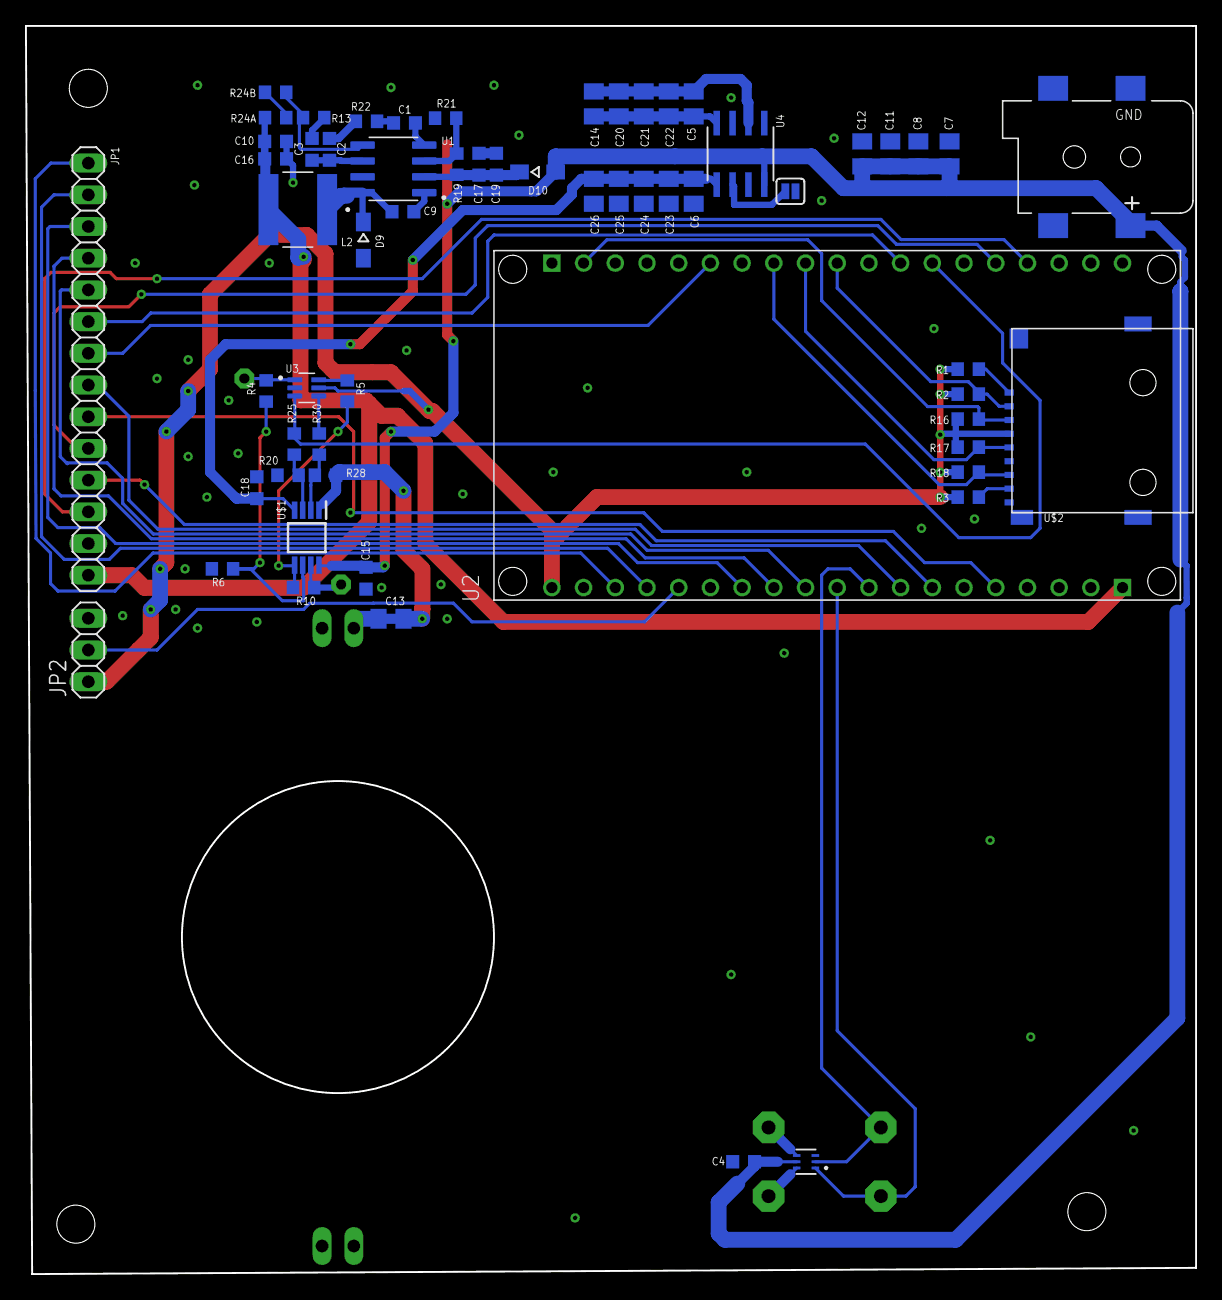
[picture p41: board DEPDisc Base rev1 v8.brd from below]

Board: 2 copper layers, 93.8 x 100.0 mm, 68 parts (60 on the bottom side), 50 nets.

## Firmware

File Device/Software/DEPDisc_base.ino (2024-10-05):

/*
  Author: Nicklas Rondot
  October 05, 2024

  Based on code by:  
  Rui Santos & Sara Santos - Random Nerd Tutorials
*/

#include "FS.h"
#include "SD.h"
#include <SPI.h>

/*  Install the "TFT_eSPI" library by Bodmer to interface with the TFT Display - https://github.com/Bodmer/TFT_eSPI
    *** IMPORTANT: User_Setup.h available on the internet will probably NOT work with the examples available at Random Nerd Tutorials ***
    *** YOU MUST USE THE User_Setup.h FILE PROVIDED IN THE LINK BELOW IN ORDER TO USE THE EXAMPLES FROM RANDOM NERD TUTORIALS ***
    FULL INSTRUCTIONS AVAILABLE ON HOW CONFIGURE THE LIBRARY: https://RandomNerdTutorials.com/cyd/ or https://RandomNerdTutorials.com/esp32-tft/   */
#include <TFT_eSPI.h>

// Install the "XPT2046_Touchscreen" library by Paul Stoffregen to use the Touchscreen - https://github.com/PaulStoffregen/XPT2046_Touchscreen
// Note: this library doesn't require further configuration
#include <XPT2046_Touchscreen.h>

TFT_eSPI tft = TFT_eSPI();

// Touchscreen pins
#define XPT2046_IRQ 36   // T_IRQ
#define XPT2046_MOSI 32  // T_DIN
#define XPT2046_MISO 39  // T_OUT
#define XPT2046_CLK 25   // T_CLK
#define XPT2046_CS 33    // T_CS

const int DEP_PIN = 4;
const int MOTOR_PIN1 = 26;
const int MOTOR_PIN2 = 27;

SPIClass touchscreenSPI = SPIClass(VSPI);
XPT2046_Touchscreen touchscreen(XPT2046_CS, XPT2046_IRQ);

#define SCREEN_WIDTH 320
#define SCREEN_HEIGHT 240
#define FONT_SIZE 4
#define FONT_SIZE_SMALL 2

// Set X and Y coordinates for center of display
const int centerX = SCREEN_WIDTH / 2;
const int centerY = SCREEN_HEIGHT / 2;
const int onethirdY = SCREEN_HEIGHT / 3;
const int twothirdsY = 2 * SCREEN_HEIGHT / 3;
const int threeQuartersY = 3 * SCREEN_HEIGHT / 4;


int mode = 0; // 0: experimental mode, 1: SD card

// Touchscreen coordinates: (x, y) and pressure (z)
int x, y, z;

// Print Touchscreen info about X, Y and Pressure (Z) on the Serial Monitor
void printTouchToSerial(int touchX, int touchY, int touchZ) {
  Serial.print("X = ");
  Serial.print(touchX);
  Serial.print(" | Y = ");
  Serial.print(touchY);
  Serial.print(" | Pressure = ");
  Serial.print(touchZ);
  Serial.println();
}


void setup() {
  Serial.begin(115200);
  pinMode(MOTOR_PIN1, OUTPUT);
  pinMode(MOTOR_PIN2, OUTPUT);

  // Start the SPI for the touchscreen and init the touchscreen
  touchscreenSPI.begin(XPT2046_CLK, XPT2046_MISO, XPT2046_MOSI, XPT2046_CS);
  touchscreen.begin(touchscreenSPI);
  // Set the Touchscreen rotation in landscape mode
  // Note: in some displays, the touchscreen might be upside down, so you might need to set the rotation to 3: touchscreen.setRotation(3);
  touchscreen.setRotation(1);

  // Start the tft display
  tft.init();
  // Set the TFT display rotation in landscape mode (flipped for assembly in housing)
  tft.setRotation(3);

  // Clear the screen before writing to it
  tft.fillScreen(TFT_BLACK);
  tft.setTextColor(TFT_BLACK, TFT_WHITE);

  //tft.fillRoundRect((centerX - 140), (onethirdY - 25), 280, 50, 10, TFT_WHITE);
  //tft.drawCentreString("Experimental mode", centerX, (onethirdY - 10), FONT_SIZE);
  tft.fillRoundRect((centerX - 140), (centerY - 25), 280, 50, 10, TFT_WHITE);
  tft.drawCentreString("Run from SD card", centerX, (centerY - 10), FONT_SIZE);
  tft.setTextColor(TFT_WHITE, TFT_BLACK);
  tft.drawCentreString("Or send data via USB", centerX, (threeQuartersY - 10), FONT_SIZE_SMALL);
}

void loop() {
  // Checks if Touchscreen was touched, and prints X, Y and Pressure (Z) info on the TFT display and Serial Monitor
  if (mode == 0 &&touchscreen.tirqTouched() && touchscreen.touched()) {
    // Get Touchscreen points
    TS_Point p = touchscreen.getPoint();
    // Calibrate Touchscreen points with map function to the correct width and height
    x = map(p.x, 200, 3700, 1, SCREEN_WIDTH);
    y = map(p.y, 240, 3800, 1, SCREEN_HEIGHT);
    z = p.z;

    printTouchToSerial(x, y, z);
    if(y < (centerY + 10) && y > (centerY - 10)){
      mode = 1;
    }

    delay(100);
  }
  if(mode == 0 && Serial.available()){
    String input = Serial.readStringUntil('\n');
    input.trim();  // Remove any leading or trailing whitespace

    // Check if the input starts with "freq"
    if (input.startsWith("freq")) {
      // Extract the value after "freq"
      int spaceIndex = input.indexOf(' ');
      if (spaceIndex != -1) {
        String valueString = input.substring(spaceIndex + 1);
        int value = valueString.toInt();

        // Perform analogWrite on pin 1 with the extracted value
        ledcDetach(DEP_PIN);
        if (value > 0) {
          ledcAttach(DEP_PIN, value, 1);
          ledcWrite(DEP_PIN, 1);
          Serial.print("Set freq to ");
          Serial.println(value);
        } else if (value == 0) {
          Serial.println("Stop DEP");
        }
      }
    }
    // Check if the input starts with "spin"
    else if (input.startsWith("spin")) {
      // Extract the value after "spin"
      int spaceIndex = input.indexOf(' ');
      if (spaceIndex != -1) {
        String valueString = input.substring(spaceIndex + 1);
        int value = valueString.toInt();

        // Perform analogWrite on pin 2 or 3 based on the value's sign
        if (value > 0) {
          analogWrite(MOTOR_PIN1, value);
          analogWrite(MOTOR_PIN2, 0);
          Serial.print("Spin forward with value ");
          Serial.println(value);
        } else if (value < 0) {
          analogWrite(MOTOR_PIN1, 0);
          analogWrite(MOTOR_PIN2, -value);  // Use the positive of the negative value
          Serial.print("Spin backward with value ");
          Serial.println(-value);
        } else if (value == 0) {
          analogWrite(MOTOR_PIN1, 0);
          analogWrite(MOTOR_PIN2, 0);
          Serial.println("Stop motor");
        }
      }
    }
  }
  if (mode == 1){
    tft.fillScreen(TFT_BLACK);
    tft.setTextColor(TFT_WHITE, TFT_BLACK);
    if(!SD.begin(5)){
      Serial.println("Card Mount Failed");
      tft.drawCentreString("No SD card connected", centerX, (centerY - 10), FONT_SIZE);
      delay(2000);
      ESP.restart();
      return;
    }
    uint8_t cardType = SD.cardType();

    if(cardType == CARD_NONE){
      Serial.println("No SD card attached");
      tft.drawCentreString("No SD card connected", centerX, (centerY - 10), FONT_SIZE);
      delay(2000);
      ESP.restart();
      mode = 0;
      return;
    }

    File file = SD.open("/run.txt");
    if(!file){
      Serial.println("Failed to open file for reading");
      tft.drawCentreString("No run.txt file exists", centerX, (centerY - 10), FONT_SIZE);
      delay(2000);
      ESP.restart();
      mode = 0;
      return;
    }

    tft.drawCentreString("Running from SD card", centerX, (centerY - 10), FONT_SIZE);
    Serial.print("Read from file: ");
    while (file.available()) {
      String input = file.readStringUntil('\n');
      input.trim();  // Remove any leading or trailing whitespace

      if (input.startsWith("delay")) {
        // Extract the value after "delay"
        int spaceIndex = input.indexOf(' ');
        if (spaceIndex != -1) {
          String valueString = input.substring(spaceIndex + 1);
          int value = valueString.toInt();
          Serial.print("Set delay to ");
          Serial.println(value);
          delay(value);
        }
      }

      // Check if the input starts with "freq"
      else if (input.startsWith("freq")) {
        // Extract the value after "freq"
        int spaceIndex = input.indexOf(' ');
        if (spaceIndex != -1) {
          String valueString = input.substring(spaceIndex + 1);
          int value = valueString.toInt();

          // Perform analogWrite on pin 1 with the extracted value
          ledcDetach(DEP_PIN);
          if (value > 0) {
            ledcAttach(DEP_PIN, value, 1);
            ledcWrite(DEP_PIN, 1);
            Serial.print("Set freq to ");
            Serial.println(value);
          } else if (value == 0) {
            Serial.println("Stop DEP");
          }
        }
      }
      // Check if the input starts with "spin"
      else if (input.startsWith("spin")) {
        // Extract the value after "spin"
        int spaceIndex = input.indexOf(' ');
        if (spaceIndex != -1) {
          String valueString = input.substring(spaceIndex + 1);
          int value = valueString.toInt();

          // Perform analogWrite on pin 2 or 3 based on the value's sign
          if (value > 0) {
            analogWrite(MOTOR_PIN1, value);
            analogWrite(MOTOR_PIN2, 0);
            Serial.print("Spin forward with value ");
            Serial.println(value);
          } else if (value < 0) {
            analogWrite(MOTOR_PIN1, 0);
            analogWrite(MOTOR_PIN2, -value);  // Use the positive of the negative value
            Serial.print("Spin backward with value ");
            Serial.println(-value);
          } else if (value == 0) {
            analogWrite(MOTOR_PIN1, 0);
            analogWrite(MOTOR_PIN2, 0);
            Serial.println("Stop motor");
          }
        }
      }
    }
    file.close();
    ESP.restart();
  }
}

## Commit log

2024-10-05 feat: started README
    [Coil 22_10_1.8 v5.sch, Coil_22_10_1.8_v9.brd, DEPDisc Base rev1 v4.sch, DEPDisc Base rev1 v5_bottom_bom.csv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]
2024-10-05 feat: completed first version of README
    [DEPDisc Base rev1 v4.sch, DEPDisc Base rev1 v5_bottom_bom.csv, DEPDisc Base rev1 v5_bottom_cpl.csv, DEPDisc Base rev1 v8.brd]
2024-10-06 feat: STLs added
    [Disc Mount (black).stl, Display Holder (black).stl, Hatch (white).stl, Inner Shell left (black).stl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]

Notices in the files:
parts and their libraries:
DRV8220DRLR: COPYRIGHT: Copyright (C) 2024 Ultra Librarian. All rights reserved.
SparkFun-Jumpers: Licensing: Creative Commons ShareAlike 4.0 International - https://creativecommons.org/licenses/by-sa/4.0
